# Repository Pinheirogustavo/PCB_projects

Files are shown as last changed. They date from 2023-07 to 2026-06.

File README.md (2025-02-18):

# PCB Projects

## Conexões presentes nas barras de pinos

### Barra de "tensoes"

- Earth: Terra virtual implementado com LM675
- VCC: +(MaxTensao da fonte utilizada / 2) Tensao NÃO regulada
- VEE:-(MaxTensao da fonte utilizada / 2)  Tensao NÃO regulada
- +9V: regulador 7809
- -9V: regulador 7909
- +5V: regulador 7805
- -5V: regulador 7905
- +3.3V: regulador 1117T-3.3

### Barra "Sinais analogicos"
- I1: corrente 1 dada pela fonte Howland
- I2: corrente 2 dada pela fonte Howland (caso bipolar)
- Ampl1: Tensão de saída condicionada do INA que monitora a corrente I1
- Ampl2: Tensão de saída condicionada do INA que monitora a corrente I2
- Sin1: Sinal alternado 1 gerado por AD9833/9850. Sem amplificação
- Sin2: Sinal alternado 2 gerado por AD9833/9850. Sem amplificação
- SinA: Sinal alternado 1 com controle de amplitude (talvez freq e fase)
- SinB: Sinal alternado 2 com controle de amplitude (talvez freq e fase)

### Barra "comunicacao"
- SINC: Sinal de sincronismo (ainda a definir)
- SDA(1-3)/SCL(1-3): Três pares de pinos reservados para comunicação - I2C
- SPI_COPI: comunicação SPI Controller Out Peripheral In
- SPI_CIPO: comunicação SPI Controller In, Peripheral Out
- SPI_clk: pino de clock que estabelece o sincronismo da comunicação SPI
- CS(x): pinos para selecionar o chip desejado (Chip Select)
> CS (AD9833): seleciona o gerador de sinais AD9833

> CS (X9c10x): seleciona o potenciometro digital do circuito de controle da corrente

###### comunicação I2C

SDA1/SCL1: implementado nos módulos "Gerador de sinais", com resistores pullup (Rp) para dispositivos de 3.3V;

SDA2/SCL2: implementado nos módulos "Fonte de corrente", com resistores pullup (Rp) para dispositivos de 5.0V. 

I2C arduino: https://docs.arduino.cc/learn/communication/wire

SPI arduino https://docs.arduino.cc/learn/communication/spi?_gl=1*1

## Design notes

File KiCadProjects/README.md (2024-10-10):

# Versao do CAD: KiCad 7.0    

Placa 900x100mm face dupla

## Dicas gerais de uso do KiCad

- Os projetos desenvolvidos na versão Kicad 7.0 não são compatíveis com versões mais recentes.

- Sempre que for alterar um projeto abra o "arquivo_pro" específico, não o arquivo geral "KiCadProjects.kicad_pro".

- Ao realizar alguma modificação de projeto elétrico (não somente design), Faça a alteração no arquivo esquemático "arquivo_sch" e depois altere o arquivo de design "arquivo_pcb" por meio da ferramenta de "atualize a PCI com as alterações feitas no esquema - F8" (símbolo no painel superior). Modificações realizadas no sentido contrário não são atualizadas no esquema e assim sua placa confeccionada não irá corresponder ao projeto elétrico criado.

- Um bom tutorial em vídeo pode ser encontrado na playlist: <https://youtube.com/playlist?list=PL3bNyZYHcRSUhUXUt51W6nKvxx2ORvUQB&si=-wXaexDJ6YDI0aJu>

- Ao criar os seus esquemas tente separar cada estágio ou módulo e evite realizar ligações diretas de "wire", pois isso irá deixar a leitura mais confusa. Ao invés disso, utilize "rótulos globais" (Ctrl L / etiqueta no painel direito), que funcionam como conectores e ainda indicam os nós dos circuitos.

## Criando simbolos, footprint e 3D  

- Editor de símbolos &rarr; Arquivo &rarr; Nova biblioteca &rarr; Global &rarr; acesse a pasta de bibliotecas do seu github &rarr; acesse a pasta dos simbolos criados por você &rarr; NOME_SIMBOLO.kicad_sym Salvar. 
 - clique em "Criar Novo Símbolo (N)" 
  
- Quando criar um novo simbolo procure seguir Reference designator: https://en.wikipedia.org/wiki/Reference_designator 
  
- Sempre utilize pinos passivos 
- Numere os pinos no desenho do símbolo, para que o footprint possa fazer a atribuição correta 
- Nome do simbolo: Duplo clique na area de trabalho &rarr; preencher o campo valor 

## Como adicionar bibliotecas  

- Bibliotecas prontas da internet (salvar em Projeto Global): https://forum.digikey.com/t/importing-the-digi-key-kicad-library-into-kicad-5-0-0/4075 
 caminho:/PCB_projects/KiCadProjects/libraries/ 
  
- Bibliotecas criadas pelo autor:  Usar o editor de simbolos e de footprint do kicad, salvar em Projeto Global.

    Caminho:/PCB_projects/KiCadProjects/libraries/MyCreates

    Já criados símbolos e footprints dos seguintes componentes:

        Módulo do gerador AD9833

        Módulo do gerador AD9850

        Módulo do Potenciômetro digital X9c10x

        Chave gangorra

- Sempre adicione as bibliotecas pelo github e não pela sua máquina local. Exemplo: 
    
 Errado: /home/name/PCB_projects/KiCadProjects/libraries/MyCreates/AD9833_module.pretty 
    
 Certo: /home/name/**github**/PCB_projects/KiCadProjects/libraries/MyCreates/AD9833_module.pretty 

 ###### Há nesse tutorial uma lista de footprints para os componentes mais comuns entre os circuitos. Utilize essa lista para garantir que haja espaço adequado a esses componentes em sua placa.

## Algumas das regras de layout PCB  - Fabricação JLCPCB

#### Todas as regras e restrições para a produção pela Jlcpcb devem ser conferidas em: <https://jlcpcb.com/capabilities/pcb-capabilities>

- largura dos segmentos de linha de corte ( Edge.cuts): 0.15 mm
  
- Tamanho de via: 0.30mm - 6.30mm diâmetro interno. Diâmetro externo deve ser no mínimo 0.20mm maior que o interno.

- Largura da trilha: mínimo de 0.16 mm (6.5 mils)

- Espaçamento entre trilhas: mínimo de 0.10 mm (4 mils)

- Espaçamento entre trilha e borda da via: mínimo de 0.10 mm (4 mils)

- Serigrafia: Largura mínima da linha de 0.16 mm (6 mils) e altura mínima do texto de 1.00 mm (40 mils).
    - Preferencialmente manter a proporção 1:6.

##### Todas essas restrições podem ser definidas por meio das "Regras de desenho" do Kicad.

 Símbolo de engrenagem (segundo no painel superior_ &rarr; Regras de desenho &rarr; tamanhos pré-definidos.
    - Permite estabelecer tamanhos de vias e trilhas que serão seguidas em todo o desenho.

 Símbolo de engrenagem (segundo no painel superior_ &rarr; Regras de desenho &rarr; restrições.
    - Permite estabalecer regras que se violadas serão indicadas pelo verificador de regras de desenho.

  Símbolo de engrenagem (segundo no painel superior_ &rarr; Texto & gráfico.
    - Permite estabelecer tamanho de Serigrafia que será seguido em todo o desenho.

##### Sempre execute o "Verificador de regras de desenho (símbolo de lista no painel superior) antes de gerar os arquivos para confecção.

- Extra: para produção na CNC - O grid deve ser maior que o diâmetro da fresa utilizada (>0,2mm).

## Orientações para layout PCB  

- Criar trilhas de alimentação, de terra e de clock. 
- Fazer as trilhas de alimentação com largura maior 
- Evitar trilhas muito longas 
- Preferir mudanças de direção de 45º nas trilhas 
- Evitar que trilhas de sinais críticos (clock e altas freqüências) fiquem paralelas por muito tempo 
- Evitar ligações diretas entre as entradas de alimentação de Cis 
- Colocar um LED indicando que a placa está energizada 
- Colocar pontos de acesso para medir com o osciloscópio 
- Usar soquetes para os CIs 
 
- Segundo ícone, ao lado do simbolo de disquete. Serve para editar as regras de furos, tamanhos de trilhas... sempre conferir. 
  
- Ícone de lista. Serve para verificar as regras RDC. 

## Alguns footprints de componentes comuns   

Resistor
    
    Resistor_THT:R_Axial_DIN0207_L6.3mm_D2.5mm_P7.62mm_Horizontal 

Capacitor eletrolítico
    
    Capacitor_THT:CP_Radial_D5.0mm_P2.50mm 

Capacitor cerâmico 
    
    Capacitor_THT:C_Disc_D3.0mm_W1.6mm_P2.50mm

Capacitor tântalo 
    
    Capacitor_THT:CP_Radial_Tantal_D4.5mm_P2.50mm 

Diodo
    
    Diode_THT:D_DO-41_SOD81_P10.16mm_Horizontal

LED 
    
    LED_THT:LED_D5.0mm 

conectores fêmea

    Connector_PinSocket_2.54mm:PinSocket_1xXX_P2.54mm_Vertical 

conectores macho 
   
    Connector_PinHeader_2.54mm:PinHeader_1xXX_P2.54mm_Vertical 

conector p4 de bateria 
    
    Connector_BarrelJack:BarrelJack_GCT_DCJ200-10-A_Horizontal 

chave gangorra
    
    Chave_Gangorra:chave gangorra 2 pinos
    
L7809
    
    Package_TO_SOT_THT:TO-220-3_Vertical
    
LM7909
    
    Package_TO_SOT_THT:TO-220-3_Vertical
    
LM675
    
    Package_TO_SOT_THT:TO-220-5_P3.4x3.7mm_StaggerOdd_Lead3.8mm_Vertical
    
L7805
    
    Package_TO_SOT_THT:TO-220-3_Vertical
    
L7905
    
    Package_TO_SOT_THT:TO-220-3_Vertical
    
LM1117T-3.3
    
    Package_TO_SOT_THT:TO-220-3_Vertical
    
AD9850
    
    Capacitor_THT:C_Disc_D3.0mm_W1.6mm_P2.50mm
    
STM32-bluepill
    
    BluePill_STM32:BluePill_STM32F103C
    
AD828
    
    AD828:AD828
    
Potenciômetro Digital X9c10x
    
    X9c10X_module:X9c10X_module
    
Arduino Nano
    
    Module:Arduino_Nano
    
AD9833
    
    AD9833_module:AD9833_module

## Tamanho de pad de componentes comuns   

###### Caso esteja usando a CNC, todos os furos podem ser configurados diretamente no FlatCAM, não sendo necessário defini-los no projeto do Kicad.

- Resistores 

>Forma da ilha: Oval
>
>Tamanho da ilha: 2,0x1,6mm
>
>Forma do furo: circular
>
>Diâmetro do furo: 0,8mm

- Capacitores eletrolíticos 

> Forma da ilha: oval(+)            retangular(-)
>
> Tamanho da ilha:2,0x1,6mm(+)      2,0x1,6mm(-)
>
> Forma do furo: circular(+)        circular(-)
>
> Diâmetro do furo: 0,8mm(+)        0,8mm(-)

- Diodos 

> Forma da ilha: oval(+)            retangular(-)
>
> Tamanho da ilha:2,0x1,6mm(+)      2,0x1,6mm(-)
>
> Forma do furo: circular(+)        circular(-)
>
> Diâmetro do furo: 0,8mm(+)        0,8mm(-) 

- LED 

> Forma da ilha: oval(+)            retangular(-)
>
> Tamanho da ilha:2,0x1,8mm(+)      1,8x1,8mm(-)
>
> Forma do furo: circular(+)        circular(-)
>
> Diâmetro do furo: 1,1mm(+)        1,1mm(-) 

- Barra de pinos 

> Forma da ilha: oval
>
> Tamanho da ilha: 2,5x1,8mm
>
> Forma do furo:circular
>
> Diâmetro do furo: 1,02
  
- Chave gangorra

> Forma da ilha: Retangular
>
> Tamanho da ilha: 2,5x7,0mm
>
> Forma do furo: oval
>
> Diâmetro do furo: 0,8x6,0mm

- Conector p4 de bateria 

    - pad1 (vin)
    
        > Forma da ilha: retangular
	
        > Tamanho da ilha: 4,6x2,0mm
	
        > Forma do furo: oval
	
        > Diâmetro do furo: 3,6x1,0mm_P2
        
    - pad2 (vee)
    
        > Forma da ilha: Oval
	
        > Tamanho da ilha: 4,2x2,0mm
	
        > Forma do furo: oval
	
        > Diâmetro do furo: 3,2x1,0mm
        
    - pad3
    
        > Forma da ilha: Oval
	
        > Tamanho da ilha: 2,0x4,2mm
	
        > Forma do furo: oval
	
        > Diâmetro do furo: 1,0x3,2mm

## Autoroteamento

-   Utilize o plugin Freerouting ou Grid Router
-   Antes de tudo sempre realize primeiramente a atualiação da PCB a partir do esquemático e a verifcação das regras de desenho
-   Caso deseje refazer o roteamento, exclua todas as trilhas e vias geradas anteriormente: Editar → Exclusões globais → Vias e trilhas/Todas as camadas.
-   Caso tenha criado uma “zona” (linha tracejada) para o plano terra, a remova antes de realizar novo Autoroteamento (Ver mais em:  [https://www.reddit.com/r/KiCad/comments/5eu7fo/freerouting_left_a_lot_of_grounds_unreachable/](https://www.reddit.com/r/KiCad/comments/5eu7fo/freerouting_left_a_lot_of_grounds_unreachable/))

## Envio para produção no JLCPCB

#### Todas as orientações para a produção pela Jlcpcb a partir do Kicad 7.0 devem ser conferidas em: <https://jlcpcb.com/help/article/how-to-generate-gerber-and-drill-files-in-kicad-7>

Em resumo, você deve gerar 3 tipos de arquivos: Gerber, de perfuração (drill) e o mapeamento do projeto.

- Gerar arquivos Gerber: Files &rarr; Fabrication outputs &rarr; Gerbers (.gbr)
    As seguintes camadas devem ser selecionadas:

        F.Cu

        F.Paste

        F.Silks

        F.Mask

        B.Cu

        B.Paste

        B.Silks

        B.Mask

        Edge.Cuts

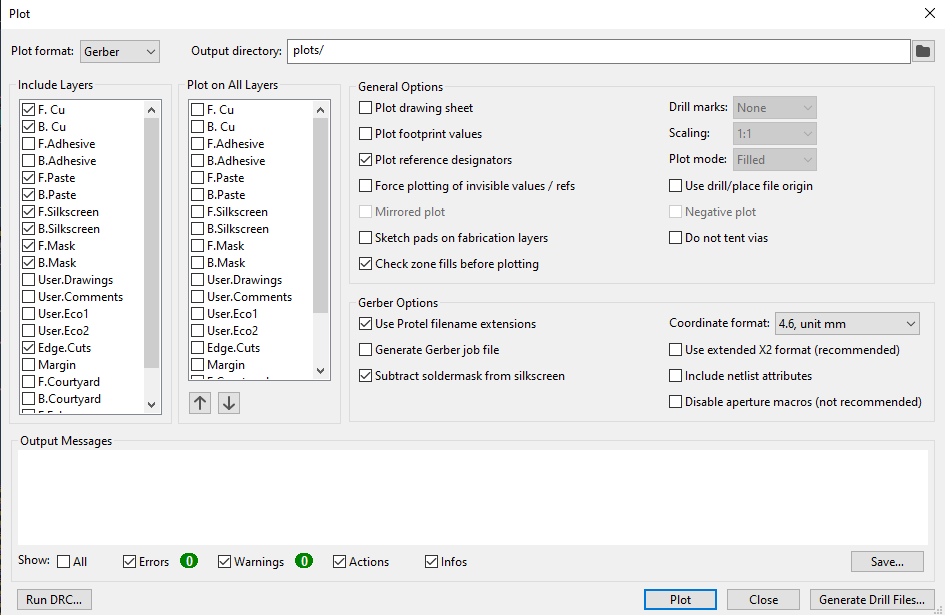
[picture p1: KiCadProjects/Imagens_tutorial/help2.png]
Camadas para gerber JLCPCB - Kicad

imagem retirada do site da JLCPCB

- Para gerar os arquivos de furo clique em "generate drill files" e siga as instruções:

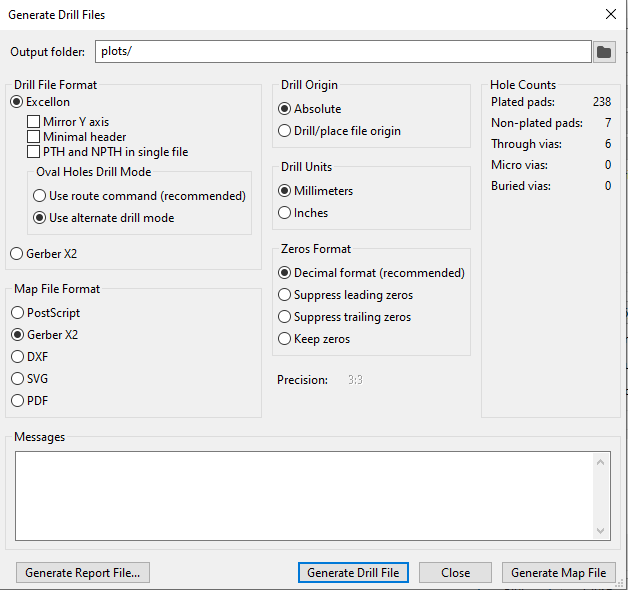
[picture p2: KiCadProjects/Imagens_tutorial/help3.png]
Furos para JLCPCB - Kicad

imagem retirada do site da JLCPCB

- Gere o arquivo de mapeamento clicando em "generate Map file".

- Todos os arquivos devem ser salvos em única pasta.

- Ao final a pasta deve conter 13 arquivos que são enviados para produção em .ZIP ou .RAR a partir da página inicial da fabricante.

#### Como produzir placas pequenas de modo repetido (Painel)

O tamanho mínimo das placas confeccionadas na JLCPCB é de 100x100mm. Caso a placa produzida seja menor, é possível copiar o design dentro de uma área definida. Há dois modos de realizar isso:

- Por meio do próprio site de encomenda do circuito. Em "PCB Specifications" selecione "Panel by JLCPCB". Ele irá captar as dimensões das linhas de "Edge.cuts" do projeto e assim você só precisa selecionar o número de linhas e colunas com repetição do projeto.

- Manualmente: Há um plugin, "Kikit", que auxilia esse trabalho. Uma vez instalado o circuito pode ser repetido por n linhas e m colunas com o uso da ferramenta "Kikit: Panelize PCB".

###### No momento de escrita desse tutorial não havia diferença de preço entre os modos de "panelização".

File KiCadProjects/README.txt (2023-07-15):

Versao do CAD: KiCad 7.0

------------------------------------------------------------------------------------------------------------------------------------------
Como adicionar bibliotecas

- Bibliotecas prontas da internet (salvar em Projeto Global): https://forum.digikey.com/t/importing-the-digi-key-kicad-library-into-kicad-5-0-0/4075
	caminho:/PCB_projects/KiCadProjects/libraries/

- Bibliotecas criadas pelo autor:  Usar o editor de simbolos e de footprint do kicad, salvar em Projeto Global
	caminho:/PCB_projects/KiCadProjects/libraries/MyCreates
------------------------------------------------------------------------------------------------------------------------------------------

Placa 90x100mm face simples

Trilhas azuis: trilhas dispostas na face de cobre inferior

Trilhas vermelhas: Representam jumpers, estao dispostas na face de cobre superior

------------------------------------------------------------------------------------------------------------------------------------------

Regras de layout PCB

- largura da trilha = 50 mils (1,27 mm)
 	O valor mínimo é de 8 mils, mas isso gera uma trilha extremamente fina
- Espaçamento entre trilhas = 50 mils (1,27 mm)
	O grid deve ser maior que o diâmetro da fresa utilizada (>0,2mm)
- Definir o algoritmo de auto-roteamento no CAD como “Grid Router” (precisa adicionar plugin)
- Definir o diâmetro do contorno em 0,5mm

------------------------------------------------------------------------------------------------------------------------------------------

Orientações para layout PCB

- Criar trilhas de alimentação, de terra e de clock.
- Fazer as trilhas de alimentação com largura maior
- Evitar trilhas muito longas
- Preferir mudanças de direção de 45º nas trilhas
- Evitar que trilhas de sinais críticos (clock e altas freqüências) fiquem paralelas por muito tempo
- Evitar ligações diretas entre as entradas de alimentação de Cis
- Colocar um LED indicando que a placa está energizada
-Colocar pontos de acesso para medir com o osciloscópio
- Usar soquetes para os CIs

------------------------------------------------------------------------------------------------------------------------------------------
Alguns footprints de componentes comuns e suas melhores  escolhas (ou até achar algo melhor)

Resistores -  11779 Resistor_THT:R_Axial_DIN0207_L6.3mm_D2.5mm_P7.62mm_Horizontal
Capacitores eletrolíticos - 525 Capacitor_THT:CP_Radial_D5.0mm_P2.50mm
Diodos -  7485 Diode_THT:D_DO-41_SOD81_P10.16mm_Horizontal
LED - 8642 LED_THT:LED_D5.0mm
conectores fêmea -  5813/6090 Connector_PinSocket_2.54mm:PinSocket_1xXX_P2.54mm_Vertical
conectores macho -  4855/5132 Connector_PinHeader_2.54mm:PinHeader_1xXX_P2.54mm_Vertical 
conector p4 de bateria - 1150 Connector_BarrelJack:BarrelJack_GCT_DCJ200-10-A_Horizontal

------------------------------------------------------------------------------------------------------------------------------------------
Tamanho de pad de componentes comuns e suas melhores  escolhas (ou até achar algo melhor). O tamanho do furo (0,8mm) não precisa ser configurado agora pois pode ser modificado na hora da produção (FlatCAM).

Resistores -  circular 2,5mm 
Capacitores eletrolíticos -  	+ circular 2mm	-retangular2x2,5mm
Diodos -   circular 2,5mm 
LED - 	+ circular 2mm	-retangular2x2,5mm
Barra de pinos - circular 2mm
conector p4 de bateria - oval3x4,2mm retangular4,6x3mm

------------------------------------------------------------------------------------------------------------------------------------------
FONTE DE TENSAO

v01;v02 SW1: Botão DPDT com trava para ligar e desligar a fonte. https://www.multcomercial.com.br/chave-push-button-7x7-com-trava.html
v03;v04 Chave gangorra kcd1 para ligar e desligar a fonte.

Os reguladores estao localizados na borda da placa, alinhados e igualmente espaçados, sendo possivel utilizar único dissipador

Segundo icone, ao lado do simbolo de disquete. Para editar as regras de furos, tamanhos de trilhas... sempre conferir. 

Icone de lista. Verifica as regras.

------------------------------------------------------------------------------------------------------------------------------------------

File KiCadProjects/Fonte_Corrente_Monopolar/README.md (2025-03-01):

# Fonte de corrente monopolar

## Versão atualmente implementada no tomógrafo: V02

## Descrição Geral do projeto

Fonte de corrente controlada por tensão monopolar do tipo Howoland aperfeiçoada. O Sistema é excitado por um sinal senoidal e fornece uma corrente alternada de amplitude constante frente uma banda de resistências. Há um sistema de monitoramento da amplitude da corrente (Ampl1) que é implementado com um circuito de condicionamento dedicado.

Estágios Fonte de Corrente: Sinal de entrada(Sin1 ou SinA) &rarr; buffer &rarr; arquitetura fonte Howland &rarr; Resistor Sentinela//Amplificador de Instrumentação &rarr;  corrente I1.

Estágios monitoramento: Amplificador de Instrumentação &rarr; AmpOp &rarr; circuito de condicionamento &rarr; amplitude da corrente Ampl1.

## Componentes do circuito:

- Amplificador Operacional Dual AD826/828: Amplificador operacional duplo implementado como buffer na entrada do sistema e de acordo com a arquitetura da fonte Howland aperfeiçoada.
	>Amplificador 1: buffer.
	
	>Amplificador 2: arquitetura da fonte Howland aperfeiçoada.
- Resistor sentinela: Resistor de baixa resistência em série com a saída da fonte Howland. Implementado para monitorar a corrente gerada.
- Amplificador de Instrumentação INA: Amplificador de Instrumentação verifica a tensão sobre o resistor sentinela e aplica alto ganho fixo. A tensão de saída é condicionada e indica a amplitude da corrente (Ampl1).  Implementado para monitorar a corrente gerada. 
- Circuito de condicionamento: Condiciona o sinal para os limites do ADC do controlador (Selecionado com jumpers nos pinos "Vref" 3.3/5V). 

## Cuidados a serem tomados

## Estágios do circuito

#### Entrada do sinal de controle de corrente:

O sinal de entrada (Vin) determina a amplitude e frequência da corrente gerada. O sistema permite dois sinais de entrada, Sin1 e SinA, que são selecionados por uma chave gangorra kcd1.

A frequência da corrente é a mesma do sinal de entrada Vin. A amplitude da corrente é dada por:

$$ I = \frac{V_{in}}{R_6} $$

#### Buffer:

Buffer implementado na entrada do sistema com o amplificador operacional dual uma vez que o circuito do gerador de sinais foi projetado sem buffer em sua saída.

#### Arquitetura fonte Howland:

Fonte monopolar do tipo Howland aperfeiçoada.

#### Resistor sentinela e amplificador de instrumentação

#### Circuito de condicionamento

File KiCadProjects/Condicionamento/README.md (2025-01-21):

# Placa de condicionamento de sinal

## Versões em produção (jlcpcb):condicionamento_compacto_V01a; condicionamento_compacto_V01b; condicionamento_Aquisicao_BIA_v03

## Descrição Geral do projeto

Circuito de condicionamento de sinal para aquisição por microcontrolador.

# Versões do projeto:

## condicionamento_compacto_V01

Circuito projetado para apenas condicionar o sinal de interesse para correta aquisição do microcontrolador utilizado, buscando não alterar nenhuma característica do sinal.

Estágios: Sinais a serem condicionados &rarr; buffer &rarr; offset (valor médio do limite de entrada do ADC) &rarr; diodos de proteção ( limites de entrada do ADC) &rarr; Filtro anti-aliasing &rarr; sinal condicionado &rarr; ADC@uC

O circuito de condicionamento permite a adequada aquisição de sinal por meio de microcontrolador, garantindo que os sinais aplicados nas entradas do dispositivo não ultrapassem os limites de tensão e corrente suportados, além da adequada amostragem do sinal, por meio de filtro anti-aliasing. Esse circuito emprega o amplificador operacional dual, o que permite o condicionamento de dois canais. Os estágios do circuito são:

- buffer: amplificador operacional no modo seguidor, configuração de alta impedância de entrada que permite o adequado acoplamento entre os estágios do sistema, minimizando a interação entre eles.

- Offset: estágio que realiza um deslocamento (offset) do sinal de entrada, adequando os sinais alternados de correntes do circuito aos ADCs do microcontrolador, adicionando um sinal DC equivalente ao valor médio do limite de entrada dos ADCS. O valor de Vref pode ser escolhido por um pino de entrada do circuito.

- Diodos de proteção: não permitem que o sinal de entrada ultrapasse  os limites de entrada do conversor ADC.

- filtro anti-alising: Frequência de corte $F_c$:

$$F_c = \frac{1}{2\cdot\pi\cdot R\cdot C} = \frac{1}{2\cdot\pi\cdot220\cdot470\cdot10 ^{-12}} = 1,5 MHz$$
**ALTERAR LEVANDO EM CONTA OS OUTROS COMPONENTES**

## condicionamento_compacto_V02

Circuito projeto para, além de condicionar o sinal de interesse para os limites de operação do microcontrolador, aplicar um ganho ao sinal de interesse em busca de melhorar a relação sinal-ruído obtida.

Estágios: Sinais a serem condicionados &rarr; buffer &rarr; amplificador não inversor com variação da resistência de entrada por controle eletrônico  &rarr; offset (valor médio do limite de entrada do ADC) &rarr; diodos de proteção ( limites de entrada do ADC) &rarr; Filtro anti-aliasing &rarr; sinal condicionado &rarr; ADC@uC

## condicionamento_Aquisicao_BIA_v01

Circuito projetado para condicionamento e aquisição de apenas 4 canais para um Analisador de Bioimpedância.

## condicionamento_Aquisicao_BIA_v02

Circuito projetado para condicionamento e aquisição de apenas 4 canais para um Analisador de Bioimpedância.

## condicionamento_Aquisicao_BIA_v03

Circuito projetado para condicionamento e aquisição de apenas 4 canais para um Analisador de Bioimpedância.

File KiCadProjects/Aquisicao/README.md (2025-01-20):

# Placa de Aquisição 

## Versão atual em produção (jlcpcb:): 01

## Descrição Geral do projeto
 As placas de aquisição tem a função de suportar os módulos de microcontroladores stm32 modelo bluepill, empregados na demodulação de sinais.

### Versão 01

Esta versão suporta até 4 módulos stm32 bluepill. Onde é possível demodular 4 ou 8 canais externos em cada módulo.

A versão de barramento suportada é:

A alimentação de cada módulo é "dedicada". Isto é, há um regulador de tensão StepDown implementado na placa que fornece a tensão de 5V (5V_stepdown), que é regulada a 3.3V (3,3V_step) que é empregada na alimentação dos módulos. Em resumo os estágios são:

VCC (barramento) &rarr; 5V (StepDown) &rarr; 3V (regulador) &rarr; entrada 3.3V bluepill

As entradas analógicas fixas de cada módulo são:

> PA1 - Amplitude da corrente I1 (Ampl1)

> PA4 - Amplitude da corrente I2 (Ampl2)

As entradas analógicas de cada módulo referentos aos canais externos são:

> PA0 - Canal X (sign_Cx)

> PB0 - Canal X+4 (sign_Cx+4)

>Estes canais externos não estão implementados no barramento, mas sim por conectores de pinos horizontais laterais identificados por "sign_C" (elementos J4 e J5).

As conexões de comunicação de cada módulo são (I2C):

> PB6 - SCL1 (3.3V)

> PB7 - SDA1 (3.3V)

As entradas digitais reservadas para sinais de sincronismo são:

> PA5 - SINC_A

> PA6 - SINC_B

> PA7 - SINC_C

> PB1 - SINCD

Assim, a ideia é que a placa opere em dois modos:

- Modo 1: leitura da amplitude de corrente individualmente em cada microcontrolador.
    Dado que o microcontrolador opera com dois ADCs, um estaria dedicado a ler algum sinal de corrente (I1 ou I2) e o segundo dedicado a ler um dos sinais vindos dos canais externos), possibilitando a leitura de 4 canais por placa de aquisição.

- Modo 2: leitura apenas dos canais externos por cada microcontrolador, sem leitura da corrente.
    Nesse modo os dois ADCs de cada microcontrolador realizam a leitura dos dois canais externos (X) e (X+4), possibilitando a leitura de 8 canais por placa de aquisição.

### Versao 02

### Versão 03

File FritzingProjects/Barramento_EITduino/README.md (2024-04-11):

# AVISO IMPORTANTE: Este Barramento está desatualizado em relação ao barramento mais recente e implementado nas novas placas do projeto. Para o barramento atualizado, ver Kicad-BarramentoV04 

O barramento para o Fritzing será atualizado o mais breve possível.

#### Esquemático

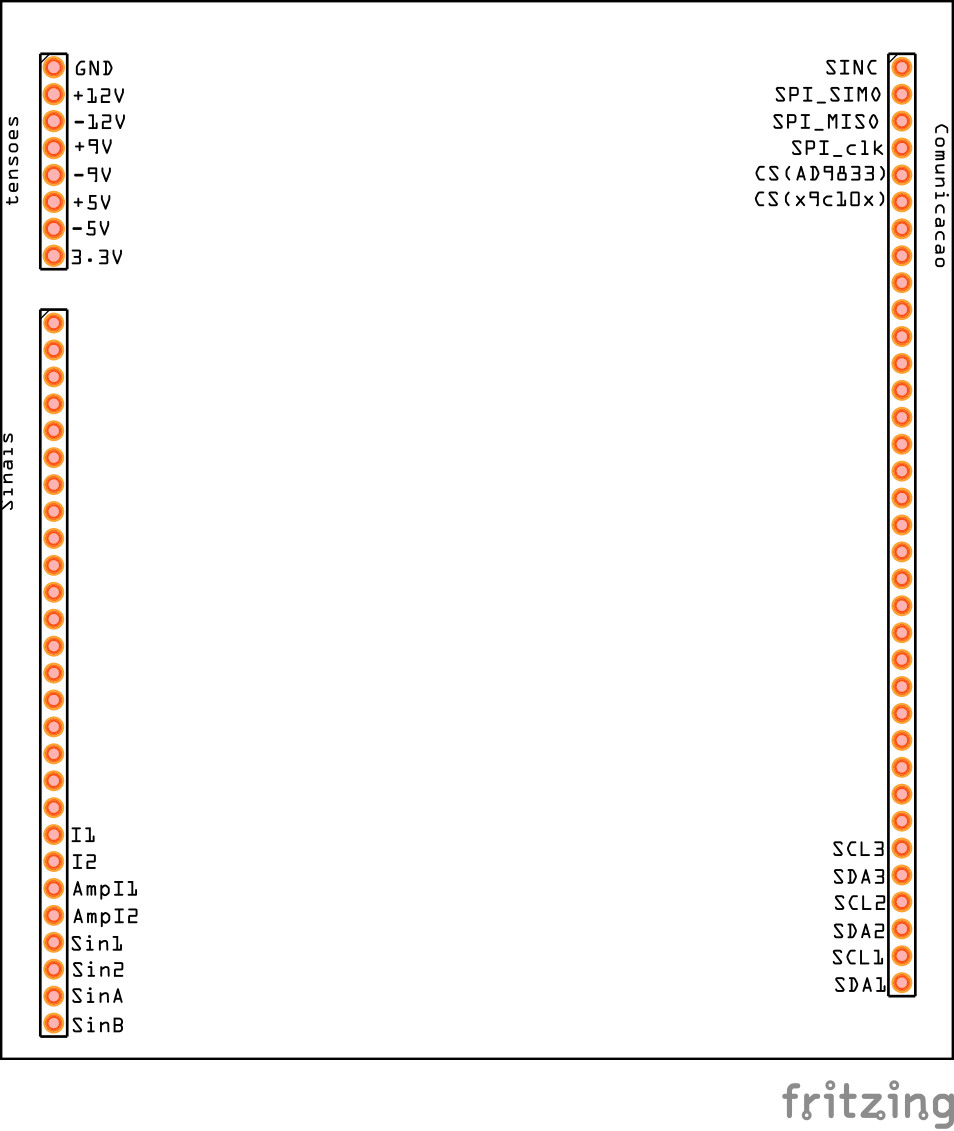
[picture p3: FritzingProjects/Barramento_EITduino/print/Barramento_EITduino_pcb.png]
Barramento EITduino - Fritzing


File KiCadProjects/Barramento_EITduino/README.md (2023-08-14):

# PCB Projects

## V01

Apresenta um único pino de terra

## V02 

- Apresenta diversos pontos de terras, separados em terras dos sinais analógicos (AGND) e terras dos sinais digitais (DGND).
- As alimentações dos circuitos analógicos foram separadas das alimentações dos circuitos digitais.

## Conexões presentes nas barras de pinos

### "tensoes"

- AGND: Terra virtual implementado com LM675 - circuitos analógicos
- DGND: Terra virtual implementado com LM675 - circuitos digitais
- VCC: +(MaxTensao da fonte utilizada / 2) Tensao NÃO regulada
- VEE:-(MaxTensao da fonte utilizada / 2)  Tensao NÃO regulada
- +9V: regulador 7809
- -9V: regulador 7909
- +5V: regulador 7805
- -5V: regulador 7905
- +3.3V: regulador 1117T-3.3

### "Sinais analogicos"
- I1: corrente 1 dada pela fonte Howland
- I2: corrente 2 dada pela fonte Howland (caso bipolar)
- Ampl1: Tensão de saída condicionada do INA que monitora a corrente I1
- Ampl2: Tensão de saída condicionada do INA que monitora a corrente I2
- Sin1: Sinal alternado 1 gerado por AD9833/9850. Sem amplificação
- Sin2: Sinal alternado 2 gerado por AD9833/9850. Sem amplificação
- SinA: Sinal alternado 1 com controle de amplitude (talvez freq e fase)
- SinB: Sinal alternado 2 com controle de amplitude (talvez freq e fase)

### "comunicacao"
- SINC: Sinal de sincronismo (ainda a definir)
- SDA(1-3)/SCL(1-3): Três pares de pinos reservados para comunicação - I2C
- SPI_COPI: comunicação SPI Controller Out Peripheral In
- SPI_CIPO: comunicação SPI Controller In, Peripheral Out
- SPI_clk: pino de clock que estabelece o sincronismo da comunicação SPI
- CS(x): pinos para selecionar o chip desejado (Chip Select)
> CS (AD9833): seleciona o gerador de sinais AD9833

> CS (X9c10x): seleciona o potenciometro digital do circuito de controle da corrente

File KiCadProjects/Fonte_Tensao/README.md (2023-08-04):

# Fonte de tensão

## Versão atual em protótipo: 03

## Descrição Geral do projeto

Sistema que a partir de uma fonte de tensão comum gera uma fonte de tensão simétrica com diferentes saídas de tensões reguladas para alimentação de todo o EITduino.

Estágios: Fonte de tensão comum ($\geqslant$ 24V) &rarr; Terra virtual &rarr; saída simétrica não regulada VCC VEE &rarr;
	> Saídas reguladas simétricas para alimentação analógica: +9V/-9V 
	> Saídas reguladas; +5V/-5V
	> Saída regulada:+3.3V

## Componentes do circuito:

- LM675
- LM78XX
- LM79XX
- LM117T-3.3

## Cuidados a serem tomados

Os reguladores da série 78XX podem ser agrupados em um único dissipador, o mesmo vale para os reguladores da série 79XX. Todos os outros dissipadores devem ser mantidos afastados pois suas carcaças não se encontram no mesmo potencial do sistema. 

O AmpOp LM675 apresenta elevada dissipação de energia, sempre utilize um dissipador de calor. 

## Estágios do circuito

#### Terra virtual

O terra virtual é feito com o amplificador operacional LM675, que fornece uma corrente máxima de 1,5A. Sua saída é simétrica em VCC +(MaxTensao da fonte utilizada / 2) e em VEE -(MaxTensao da fonte utilizada / 2).

Essas tensões não são reguladas, sofrendo oscilações e não devem ser utilizadas para alimentação de outros subsistemas do EITduino.

#### Reguladores 78XX

Reguladores de tensão positivos que também fornecem corrente máxima de 1,5A. São utilizados CIs que fornecem +9V e +5V.

#### Reguladores 79XX

Reguladores de tensão negativos que também fornecem corrente máxima de 1,5A. São utilizados CIs que fornecem -9V e -5V.

#### Regulador LM117T-3.3

Regulador de tensão positivo que  fornece corrente máxima de 800mA. Fornece +3.3V.

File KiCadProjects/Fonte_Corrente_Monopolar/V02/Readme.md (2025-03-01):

### Os esquemático e visão-3D podem ser conferidos em alta resolução na pasta [print](https://github.com/Pinheirogustavo/PCB_projects/tree/main/KiCadProjects/Fonte_Corrente_Monopolar/V02/print)

## Esquemático

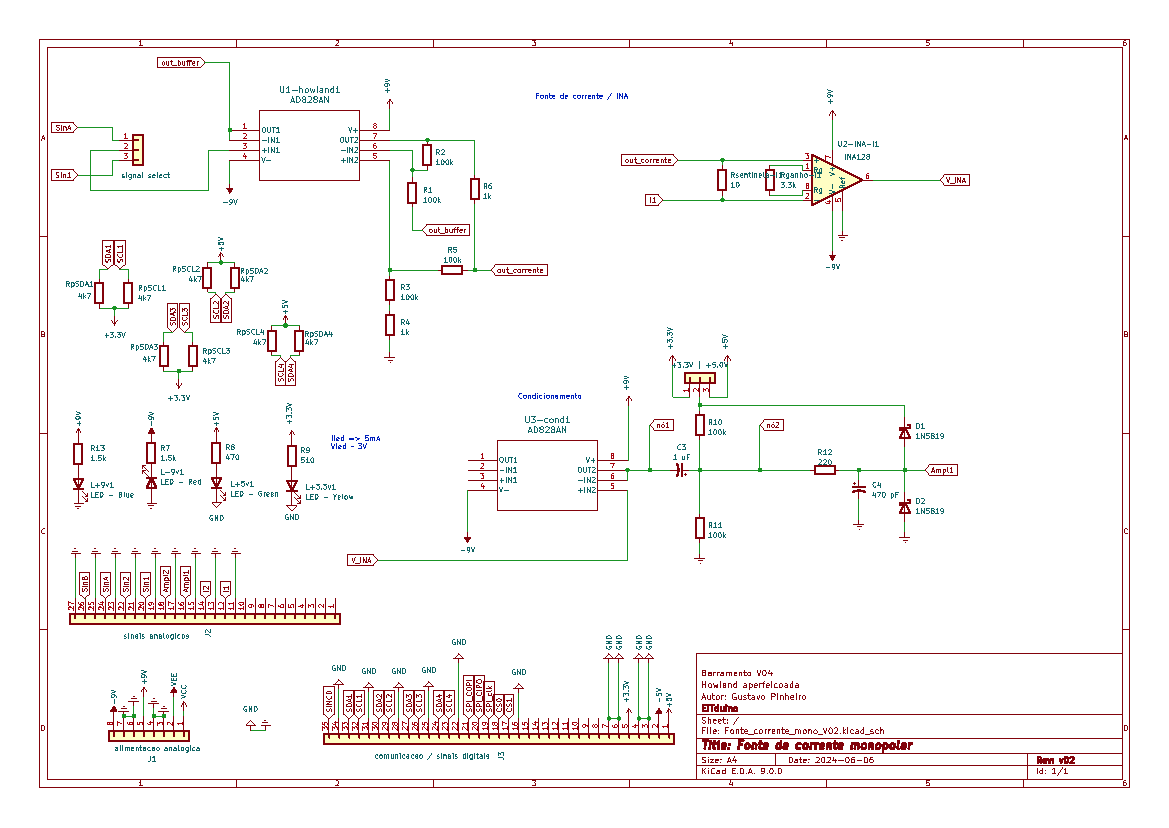
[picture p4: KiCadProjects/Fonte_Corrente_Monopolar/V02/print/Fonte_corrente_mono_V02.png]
Fonte de corrente howland aperfeiçoada monopolar - Kicad


## PCB-3D

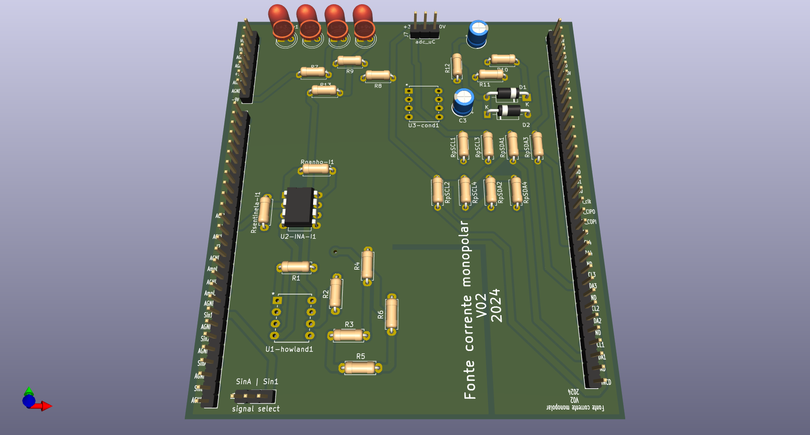
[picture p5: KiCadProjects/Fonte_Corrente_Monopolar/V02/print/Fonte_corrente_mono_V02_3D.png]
Fonte de corrente howland aperfeiçoada monopolar - PCB 3D Kicad


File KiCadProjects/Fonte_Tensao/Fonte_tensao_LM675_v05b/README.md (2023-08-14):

# V02

- Diversos pontos de terras, separados em terras dos sinais analógicos (AGND) e terras dos sinais digitais (DGND).
- As alimentações dos circuitos analógicos foram separadas das alimentações dos circuitos digitais.

# Esquemático

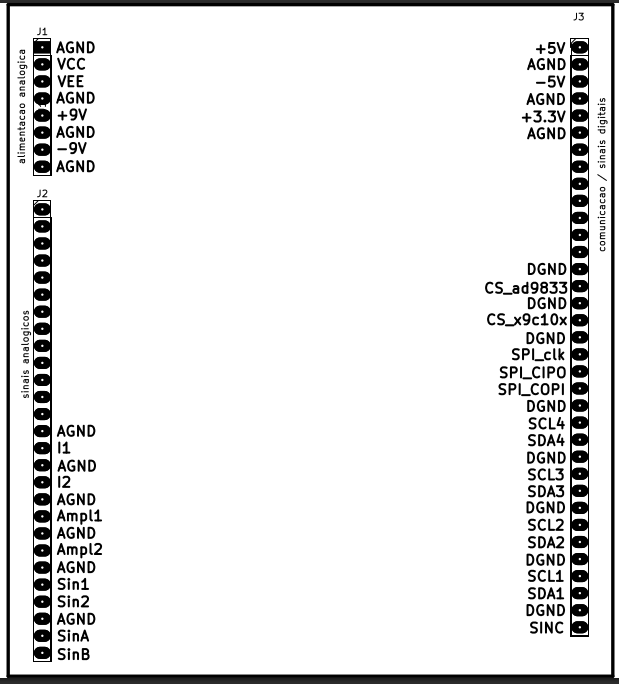
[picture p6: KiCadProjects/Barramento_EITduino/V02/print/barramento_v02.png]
Barramento EITduino V02 preto e branco - Kicad


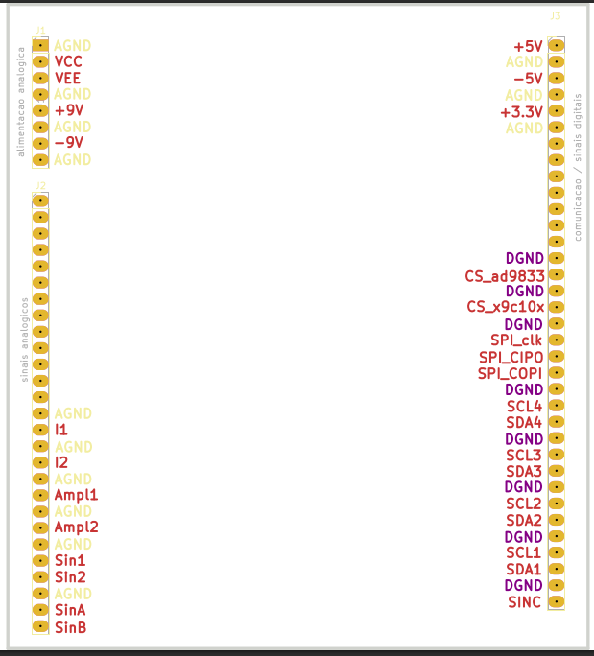
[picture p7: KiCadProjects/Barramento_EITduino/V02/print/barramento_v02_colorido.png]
Barramento EITduino V02 colorido - Kicad


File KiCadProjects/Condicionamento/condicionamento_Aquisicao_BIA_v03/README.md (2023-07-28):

# Circuito de condicionamento e aquisição de sinal

## Descrição Geral do projeto

Sistema projetado para permitir a aquisição de sinais por meio dos dois ADCs presentes em cada microcontrolador STM32.

Estágios: Sinais a serem condicionados &rarr; buffer &rarr; offset (valor médio do limite de entrada do ADC) &rarr; diodos de proteção ( limites de entrada do ADC) &rarr; Filtro anti-aliasing &rarr; sinal condicionado &rarr; ADC@STM32

## Sinais do circuito:

- AmplI1: Tensão de saída **já condicionada** do INA que monitora a corrente I1
- Amp_E1: Tensão medida pelo eletrodo proximal do pé/mão
- Amp_E2: Tensão medida pelo eletrodo proximal do pé/mão

##Cuidados a serem tomados

O conjunto de pinos **Vref** permite selecionar sinais e 3.3V e 5.0V. A escolha do sinal deve ser adequada ao limite de entrada dos pinos ADCs do microcontrolador utilizado. Para o STM32 esse limite é de 3.3V.

Todos os sinais que são enviados aos pinos de ADCs dos microcontroladores devem estar devidamente condicionados.

Sobre a alimentação dos microcontroladores: O par de pinos "alimentacao_Master" fornece uma alimentação de +5V  ao Master quando é fechado. Esse  par de pinos deve permanecer aberto quando o microcontrolador Master estiver conectado ao computador por meio de cabo USB, pois o pino de 5V do STM32 é diretamente conectada à alimentação fornecida por USB, sem qualquer circuito de proteção. O microcontrolador Slave está sempre conectado à alimentação de 5V do sistema. Somente conecte esse dispositivo ao computador se o sistema estiver desligado. 

## Estágios do circuito

#### Circuito de condicionamento

O circuito de condicionamento permite a adequada aquisição de sinal por meio de microcontrolador, garantindo que os sinais aplicados nas entradas do dispositivo não ultrapassem os limites de tensão e corrente suportados, além da adequada amostragem do sinal, por meio de filtro anti-aliasing. Esse circuito emprega o amplificador operacional dual AD826/828, o que permite o condicionamento de dois canais. Os estágios do circuito são: 

- buffer: amplificador operacional no modo seguidor, configuração de alta impedância de entrada que permite o adequado acoplamento entre os estágios do sistema, minimizando a interação entre eles.

- Offset: estágio que realiza um deslocamento (offset) do sinal de entrada, adequando os sinais alternados de correntes do circuito aos ADCs do microcontrolador, adicionando um sinal DC equivalente ao valor médio do limite de entrada dos ADCS. O valor de Vref deve ser definido pelo operador de acordo com esse limite.

- Diodos de proteção: não permitem que o sinal de entrada ultrapasse  os limites de entrada do conversor ADC. O valor de Vref deve ser definido pelo operador de acordo com esse limite.

- filtro anti-alising: Frequência de corte $F_c$:

$$F_c = \frac{1}{2\cdot\pi\cdot R\cdot C} = \frac{1}{2\cdot\pi\cdot220\cdot470\cdot10 ^{-12}} = 1,5 MHz$$

#### Microcontroladores

Dois microcontroladores são empregados nesse sistema de BIA, permitindo a leitura de 4 canais de medição. A comunicação entre eles é feita por meio do protocolo I2C. Ambos leem o sinal de amplitude da corrente medida pelo INA (AmpI1) em seus ADCs.

- STM32 Master

O par de pinos "alimentacao_Master" fornece uma alimentação de +5V quando é fechado. Esse  par de pinos deve permanecer aberto quando o microcontrolador estiver conectado ao computador por meio de cabo USB, pois o pino de 5V do STM32 é diretamente conectada à alimentação fornecida por USB, sem qualquer circuito de proteção.

> ADC1: Pino B0 recebe o sinal de amplitude de corrente AmpI1

> ADC2: Pino B1 recebe o sinal de amplitude de tensão do eletrodo de medição E1.

- STM32 Slave

O microcontrolador está sempre conectado à alimentação de 5V do sistema. Somente conecte esse dispositivo ao computador se o sistema estiver desligado. 

> ADC1: Pino B0 recebe o sinal de amplitude de corrente AmpI1

> ADC2: Pino B1 recebe o sinal de amplitude de tensão do eletrodo de medição E2.

## Esquemático

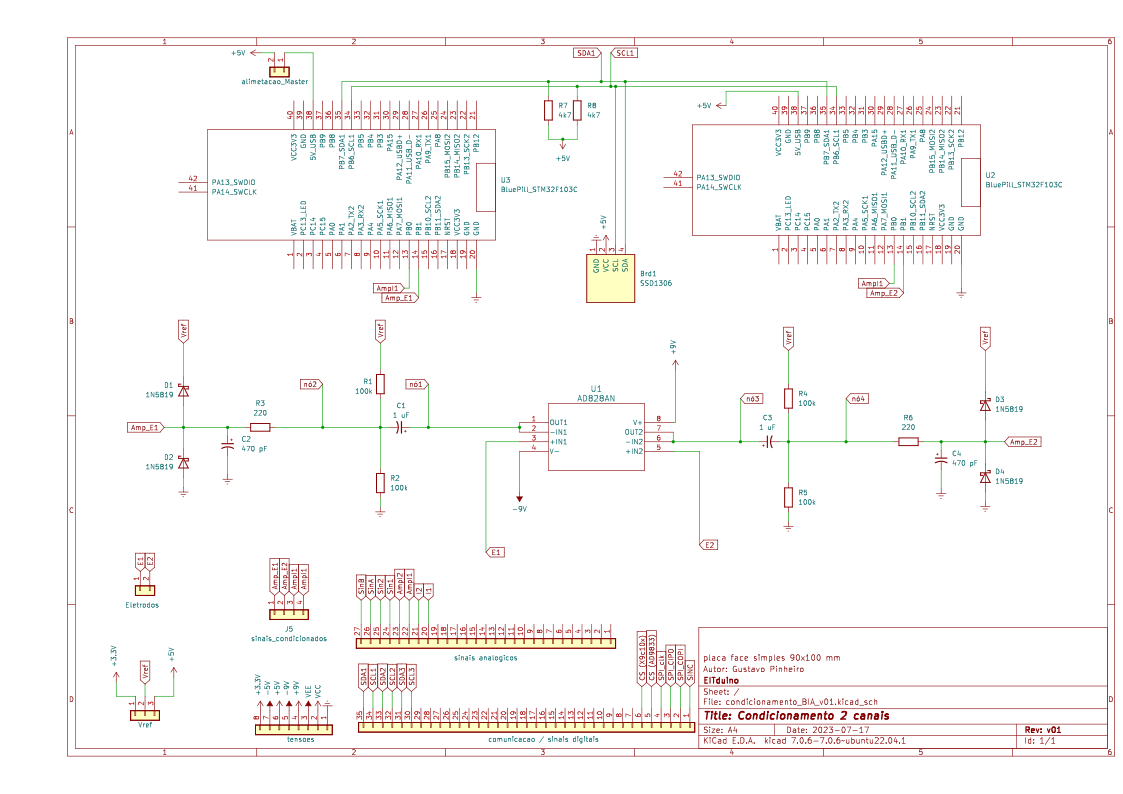
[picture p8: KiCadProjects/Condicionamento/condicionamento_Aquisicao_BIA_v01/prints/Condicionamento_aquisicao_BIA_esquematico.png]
Legenda Esquematico- Kicad


## PCB

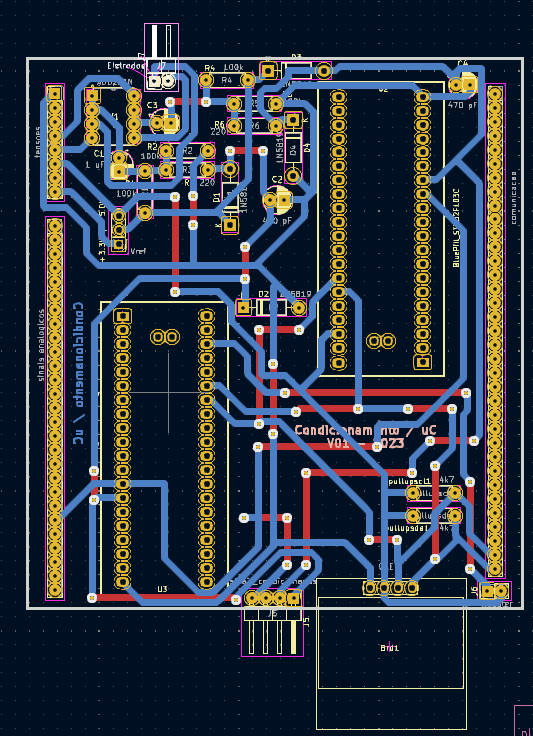
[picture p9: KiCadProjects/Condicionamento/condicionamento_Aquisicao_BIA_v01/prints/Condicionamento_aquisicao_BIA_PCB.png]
Legenda PCB- Kicad


## PCB-3D

legenda PCB 3D - Kicad

## PCB Máscara

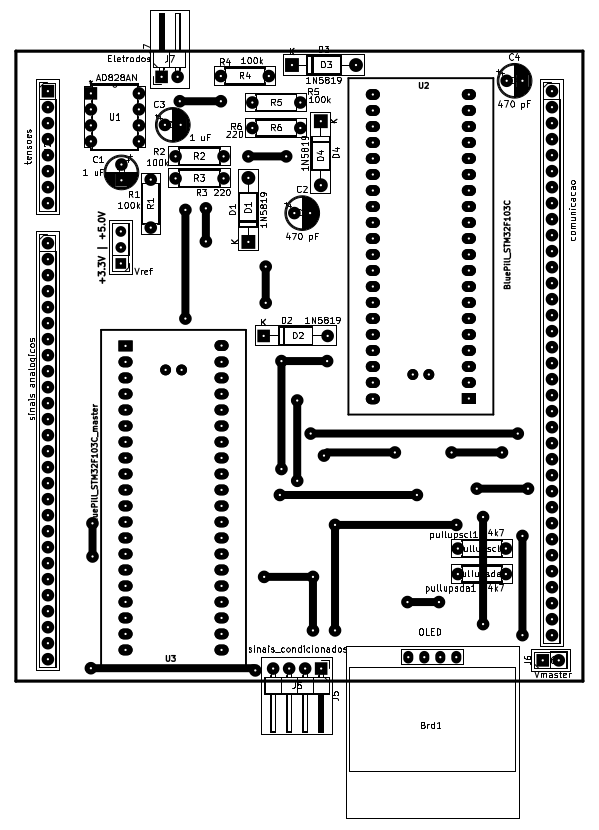
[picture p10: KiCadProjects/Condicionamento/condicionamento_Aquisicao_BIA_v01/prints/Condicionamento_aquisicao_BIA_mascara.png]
legenda PCB Máscara - Kicad


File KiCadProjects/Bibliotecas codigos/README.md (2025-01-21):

# Bibliotecas para uso de microcontroladores (.h)

Aqui estão reunidas todas as bibliotecas empregadas nos microcontroladores presentes no projeto de tomógrafo por impedância elétrica desse repositório. A intenção é permitir que se rastreie quais versões das bibliotecas estão implementadas nesse projeto, visto que elas são utilizadas e modificadas por outros pesquisadores do grupo.

A seguir a descrição dessas bibliotecas:

## AD9833.h

> Autoria: Bill Williams

> Modificado por: não modificado

Biblioteca para controle do módulo gerador de onda AD9833 por meio de comunicação SPI. Funciona apenas com o microcontrolador Arduino Nano. **É necessário, como próximo passo, adaptá-la para o microcontrolador stm32**.

## ad9850.h

> Autoria:  Erick León

> Modificado por: Gustavo Pinheiro

Biblioteca para controle do módulo gerador de onda AD9850 por meio de saídas digitais de um microcontrolador qualquer. As únicas alterações foram justamente nos pinos digitais utilizados em cada projeto de placa.

**Para futuras aplicações** deve-se apenas alterar os pinos digitais utilizados para o controle (linhas 8 a 11).

## demux.h

> Autoria: Gustavo Pinheiro

> Modificado por:

Biblioteca para o uso da placa demux "Demux.V01". Permitindo selecionar os canais de injeção e drenagem de corrente num universo de 128 eletrodos.

A seleção do canal é feita a partir de um byte, dividido da seguinte forma:

> In (injeção): 0000 0000 to 0111 1111 or 00 to 7F or 0 to 127

> Out (drenagem): 1000 0000 to 1111 1111 or 80 to FF or 128 to 255

Uma  pode ser encontrada em:
Você pode consultar uma [tabela ASCII](https://web.cecs.pdx.edu/~harry/compilers/ASCIIChart.pdf) para verificar o valor hexadecimal de um eletrodo específico, uma vez que os bytes enviados pela comunicação I2C estão nesse formato.

**Atualmente os projetos de placas se limitam a 32 canais, 5 mux's em cascata. A integração de mais placas ou aumento de canais em cada uma delas necessita de alteração da Biblioteca para expansão na manipulação dos bits**

## dft.h

> Autoria:  Erick León

> Modificado por:

A Biblioteca permite o cálculo de uma componente da DFT de um sinal qualquer, se amostrado um sinal com ciclos completos (ou seja, em uma frequência que seja múltipla inteira da frequência de amostragem).

Retorna:

> Valor medio do sinal

> A amplitude do sinal

> A fase do sinal

## gerador.h

> Autoria: Gustavo Pinheiro

> Modificado por:

A Biblioteca permite controlar a placa de gerador de sinais "AD9850.V01", alterando a frequência do sinal emitido pelo módulo ad9850 e controle do ganho de sinal, por meio de alteração do potenciômetro implementado no amplificador inversor.

As funções presentes são:

> incrementa_frequencia(): Aumenta a frequência do sinal emitido, percorrendo um array de valores.

> decrementa_frequencia(): Diminui a frequência do sinal emitido, percorrendo um array de valores.

> aumenta_ganho(): Aumenta o ganho do sinal emitido, percorrendo para baixo os valores do potenciômetro digital (wiper_down).

> diminui_ganho(): Diminui o ganho do sinal emitido, percorrendo para cima os valores do potenciômetro digital (wiper_up).

> ganho_minimo(): Configura o circuito para o ganho mínimo possível.

> ganho_maximo(): Configura o circuito para o ganho máximo possível.

> printa_dados(): Exibe no monitor serial os valores de resitência do potenciômetro digital e a frequência do sinal atuais.

## serial_debug.h

> Autoria: Erick León

> Modificado por:

## stm32_adc_dual_mode.h

> Autoria: Erick León

> Modificado por:

Biblioteca para uso do ADC do STM32F103.

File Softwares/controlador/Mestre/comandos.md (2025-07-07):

Lista de comandos para o programa de controle mestre EIT "Mestre.ino"
# Comandos de seleção de frequências

- **1**: altera a frequência do sinal para **200 kHz**; n_pontos_base = 3; n_pontos_mult = 2 (= 2 ciclos); tempo de demodulacao = 2.

- **2**: altera a frequência do sinal para **125 kHz**; n_pontos_base = 24; n_pontos_mult = 1 (= 5 ciclos); tempo de demodulacao = 10.

- **3**: altera a frequência do sinal para **100 kHz**; n_pontos_base = 6; n_pontos_mult = 2 (= 2 ciclos); tempo de demodulacao = 5.

- **4**: altera a frequência do sinal para **50 kHz**; n_pontos_base = 12; n_pontos_mult = 2 (= 2 ciclos); tempo de demodulacao = 10.

- **5**: altera a frequência do sinal para **5 kHz**; n_pontos_base = 120; n_pontos_mult = 2 (= 2 ciclos); tempo de demodulacao = 10.

# Parâmetros de demodulação

- **-**: Diminui o tempo de demodulação.

- **+**: Aumenta o tempo de demodulação.

- **t**: Diminui número de pontos da demodulação.

- **u**: Aumenta número de pontos da demodulação.

# Controle de eletrodos

- **a**: Injeta nos eletrodos 0 e 1.

- **b**: Injeta nos eletrodos 1 e 2.

- **c**: Injeta nos eletrodos 2 e 3.

- **w**: Diminui padrão de injeção.

- **z**: Aumenta padrão de injeção.

# Modos de leitura

- **i**: Inicia as medidas dos eletrodos.

- **v**: Pega os valores lidos pelos eletrodos.

- **f**: Pega um frame da leitura.

- **m**: Pega um frame da leitura e exibe a matriz.

- **j**:

- **k**:

- **l**:

- **s**:

# Controle de amplitude do sinal

- **L**: Diminui a amplitude do sinal.

- **U**: Aumenta a amplitude do sinal.

- **S**: Salva o ganho do sinal.

- **x**: Reduz o sinal ao ganho mínimo.

- **y**: Aumenta o sinal ao ganho máximo.

- **p**: Imprime os dados do sinal: Valor do resistor de ganho (Rs); frequência atual; ganho atual; tensão de saida ideal.

# xxxxx

- **adicionar enderecos dos dispositivos**:

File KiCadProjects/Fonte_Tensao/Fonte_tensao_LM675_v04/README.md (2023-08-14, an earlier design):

# Fonte de tensão

## Especificidades da versão

A base do barramento é a  [versão 2 do barramento EITduino](https://github.com/Pinheirogustavo/PCB_projects/tree/main/KiCadProjects/Barramento_EITduino/V02)

LED vermelho: indica que uma fonte externa está conectada e acionada.

LED verde: indica o funcionamento do circuito de terra virtual.

Foram adicionados diversos pinos de terra AGND e DGND em relação às versões anteriores.

## Cuidados a serem tomados

## Esquemático

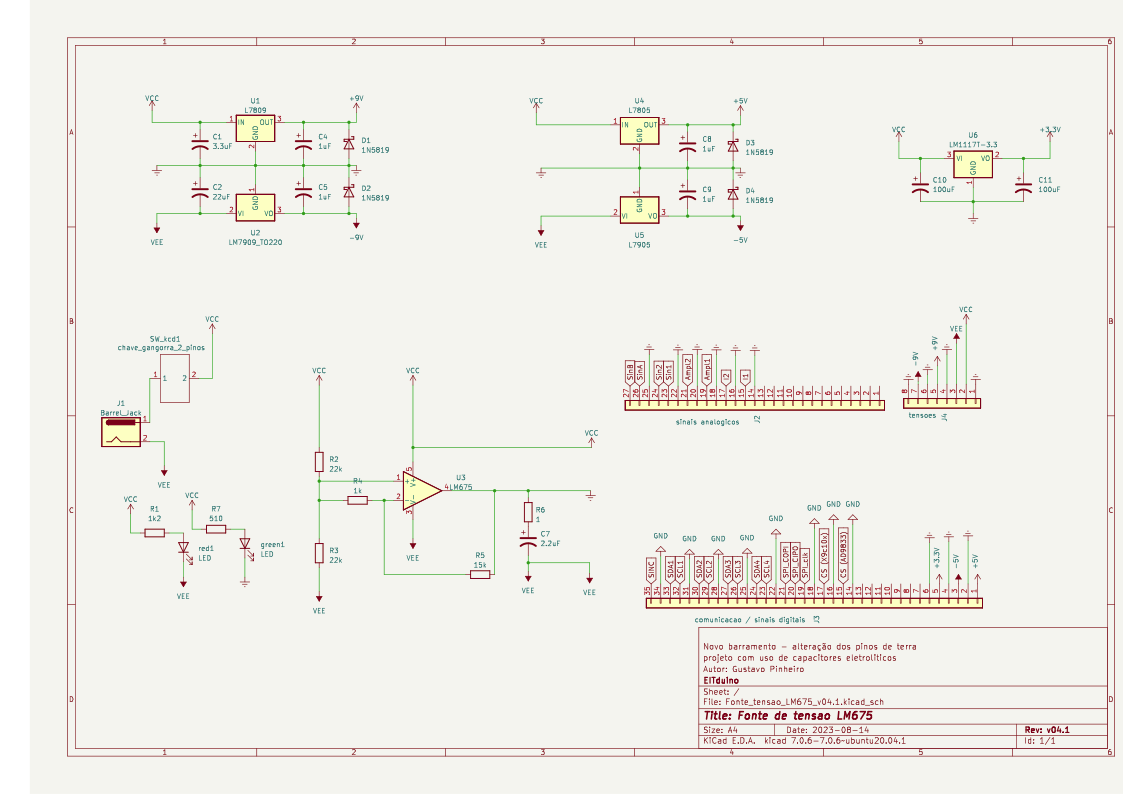
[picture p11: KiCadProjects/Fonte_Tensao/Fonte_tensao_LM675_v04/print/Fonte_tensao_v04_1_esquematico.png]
Legenda Esquematico- Kicad


## PCB

Legenda PCB- Kicad

## PCB-3D

legenda PCB 3D - Kicad

## PCB Máscara

legenda PCB Máscara - Kicad

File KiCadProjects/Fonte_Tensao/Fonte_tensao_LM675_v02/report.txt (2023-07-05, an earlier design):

Traçado para '/home/gustavo/Dropbox/KiCadProjects/Fonte_Tensao/Fonte_tensao_LM675_v02/gerbers/Fonte_tensao_LM675-F_Cu.gbr'.
Traçado para '/home/gustavo/Dropbox/KiCadProjects/Fonte_Tensao/Fonte_tensao_LM675_v02/gerbers/Fonte_tensao_LM675-B_Cu.gbr'.
Traçado para '/home/gustavo/Dropbox/KiCadProjects/Fonte_Tensao/Fonte_tensao_LM675_v02/gerbers/Fonte_tensao_LM675-F_Paste.gbr'.
Traçado para '/home/gustavo/Dropbox/KiCadProjects/Fonte_Tensao/Fonte_tensao_LM675_v02/gerbers/Fonte_tensao_LM675-B_Paste.gbr'.
Traçado para '/home/gustavo/Dropbox/KiCadProjects/Fonte_Tensao/Fonte_tensao_LM675_v02/gerbers/Fonte_tensao_LM675-F_Silkscreen.gbr'.
Traçado para '/home/gustavo/Dropbox/KiCadProjects/Fonte_Tensao/Fonte_tensao_LM675_v02/gerbers/Fonte_tensao_LM675-B_Silkscreen.gbr'.
Traçado para '/home/gustavo/Dropbox/KiCadProjects/Fonte_Tensao/Fonte_tensao_LM675_v02/gerbers/Fonte_tensao_LM675-F_Mask.gbr'.
Traçado para '/home/gustavo/Dropbox/KiCadProjects/Fonte_Tensao/Fonte_tensao_LM675_v02/gerbers/Fonte_tensao_LM675-B_Mask.gbr'.
Traçado para '/home/gustavo/Dropbox/KiCadProjects/Fonte_Tensao/Fonte_tensao_LM675_v02/gerbers/Fonte_tensao_LM675-Edge_Cuts.gbr'.
Arquivo de trabalho do Gerber '/home/gustavo/Dropbox/KiCadProjects/Fonte_Tensao/Fonte_tensao_LM675_v02/gerbers/Fonte_tensao_LM675-job.gbrjob' foi criado.
Informação: Feito.

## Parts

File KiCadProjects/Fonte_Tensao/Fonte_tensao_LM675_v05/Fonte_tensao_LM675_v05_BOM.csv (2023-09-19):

Id | Designador | Footprint | Quantidade | Designação | Fornecedor e referência | itens para 5 placas?
1 | D1,D4,D3,D2 | D_DO-41_SOD81_P10.16mm_Horizontal | 4 | 1N5819 |  | ok
2 | C5 | C_Disc_D3.0mm_W1.6mm_P2.50mm | 1 | 220nF |  | n
3 | R7 | R_Axial_DIN0207_L6.3mm_D2.5mm_P7.62mm_Horizontal | 1 | 1 |  | Somente 10 ohms
4 | U2 | TO-220-3_Vertical | 1 | LM7909_TO220 |  | n
5 | R5 | R_Axial_DIN0207_L6.3mm_D2.5mm_P7.62mm_Horizontal | 1 | 1k |  | n
6 | C4,C1,C10,C7 | CP_Radial_Tantal_D4.5mm_P2.50mm | 4 | 1uF
7 | C8 | CP_Radial_Tantal_D4.5mm_P2.50mm | 1 | 10uF
8 | R3,R4 | R_Axial_DIN0207_L6.3mm_D2.5mm_P7.62mm_Horizontal | 2 | 22k |  | n
9 | U3 | TO-220-5_P3.4x3.7mm_StaggerOdd_Lead3.8mm_Vertical | 1 | LM675
10 | I/0 | chave gangorra 2 pinos | 1 | Vin
11 | green1,red1 | LED_D5.0mm | 2 | LED
12 | J3 | PinHeader_1x35_P2.54mm_Vertical | 1 | comunicacao / sinais digitais
13 | C9 | CP_Radial_Tantal_D4.5mm_P2.50mm | 1 | 33uF
14 | C11,C2 | CP_Radial_Tantal_D4.5mm_P2.50mm | 2 | 2.2uF
15 | U5 | TO-220-3_Vertical | 1 | L7905
16 | J1 | PinHeader_1x08_P2.54mm_Vertical | 1 | alimentacao analogica
17 | J2 | PinHeader_1x27_P2.54mm_Vertical | 1 | sinais analogicos
18 | U6 | TO-220-3_Vertical | 1 | LM1117T-3.3
19 | C3,C12 | C_Disc_D3.0mm_W1.6mm_P2.50mm | 2 | 100 nF
20 | R2 | R_Axial_DIN0207_L6.3mm_D2.5mm_P7.62mm_Horizontal | 1 | 510 |  | n
21 | R6 | R_Axial_DIN0207_L6.3mm_D2.5mm_P7.62mm_Horizontal | 1 | 15k |  | n
22 | U1 | TO-220-3_Vertical | 1 | L7809
23 | U4 | TO-220-3_Vertical | 1 | L7805
24 | Vin | BarrelJack_GCT_DCJ200-10-A_Horizontal | 1 | Vin
25 | R1 | R_Axial_DIN0207_L6.3mm_D2.5mm_P7.62mm_Horizontal | 1 | 1k2 |  | n

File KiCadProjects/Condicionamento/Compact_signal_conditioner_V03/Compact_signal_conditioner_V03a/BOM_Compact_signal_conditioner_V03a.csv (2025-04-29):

Reference | Qty | Value | DNP | Exclude from BOM | Exclude from Board | Footprint | Datasheet
C1,C4 | 2 | 470 pF |  |  |  | Capacitor_THT:CP_Radial_D5.0mm_P2.50mm | ~
C2,C3 | 2 | 1 uF |  |  |  | Capacitor_THT:CP_Radial_D5.0mm_P2.50mm | ~
D1,D2,D3,D4 | 4 | 1N5819 |  |  |  | Diode_THT:D_DO-41_SOD81_P10.16mm_Horizontal | http://www.vishay.com/docs/88525/1n5817.pdf
J1 | 1 | Conn_02x09_Top_Bottom |  |  |  | Connector_PinSocket_2.54mm:PinSocket_2x09_P2.54mm_Horizontal | ~
J2 | 1 | Canais-eletrodos |  |  |  | Connector_PinHeader_2.54mm:PinHeader_1x02_P2.54mm_Vertical | ~
J5 | 1 | in |  |  |  | Connector_PinSocket_2.54mm:PinSocket_1x06_P2.54mm_Horizontal | ~
J6 | 1 | In_1 select |  |  |  | Connector_PinHeader_2.54mm:PinHeader_1x03_P2.54mm_Vertical | ~
J7 | 1 | In_2 select |  |  |  | Connector_PinHeader_2.54mm:PinHeader_1x03_P2.54mm_Vertical | ~
J8 | 1 | out |  |  |  | Connector_PinHeader_2.54mm:PinHeader_1x06_P2.54mm_Horizontal | ~
R1,R8 | 2 | 220 |  |  |  | Resistor_THT:R_Axial_DIN0207_L6.3mm_D2.5mm_P7.62mm_Horizontal | ~
R2,R3,R4,R5 | 4 | 100k |  |  |  | Resistor_THT:R_Axial_DIN0207_L6.3mm_D2.5mm_P7.62mm_Horizontal | ~
RC1,RC2,RC3,RC4,RC5,RC6,RC7,RC8,RC9,RC10 | 10 | R |  |  |  | Resistor_THT:R_Axial_DIN0207_L6.3mm_D2.5mm_P7.62mm_Horizontal | ~
Rfg_1,Rfg_2 | 2 | 51k |  |  |  | Resistor_THT:R_Axial_DIN0207_L6.3mm_D2.5mm_P7.62mm_Horizontal | ~
U1,U2 | 2 | CD4066BE |  |  |  | Package_DIP:DIP-14_W7.62mm | https://www.ti.com/lit/ds/symlink/cd4066b.pdf
U1-buffer1,U2-gain1,U3-Cond-DIP1 | 3 | AD828AN |  |  |  | AD828:N_8_ADI | AD828AN
U4-Cond-SMD1,U5-buffer1,U6-gain1 | 3 | AD8056ARZ |  |  |  | AD8056:R_8_ADI | AD8056ARZ

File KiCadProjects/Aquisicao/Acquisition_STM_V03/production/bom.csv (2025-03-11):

Designator | Footprint | Quantity | Value | LCSC Part #
C1 | CP_Radial_D5.0mm_P2.50mm | 1 | 680u
C2 | CP_Radial_D5.0mm_P2.50mm | 1 | 220u
C3 | CP_Radial_Tantal_D4.5mm_P2.50mm | 1 | 10uF
C4 | CP_Radial_Tantal_D4.5mm_P2.50mm | 1 | 33uF
D1 | D_DO-41_SOD81_P10.16mm_Horizontal | 1 | 1N5819
J1 | PinHeader_1x08_P2.54mm_Vertical | 1 | alimentacao analogica
J10 | PinHeader_2x08_P2.54mm_Vertical | 1 | gpio-U1
J11 | PinHeader_2x08_P2.54mm_Vertical | 1 | gpio-U2
J12 | PinHeader_2x08_P2.54mm_Vertical | 1 | gpio-U3
J13 | PinHeader_2x08_P2.54mm_Vertical | 1 | gpio-U4
J14, J15, J16, J17, J18, J19, J8, J9 | PinHeader_2x05_P2.54mm_Horizontal | 8 | Conn_02x05_Top_Bottom
J2 | PinHeader_1x27_P2.54mm_Vertical | 1 | sinais analogicos
J3 | PinHeader_1x35_P2.54mm_Vertical | 1 | comunicacao / sinais digitais
L+3.3V1 | LED_D5.0mm | 1 | LED Yelow
L1 | L_7.3x7.3_H4.5 | 1 | 33u
R1 | R_Axial_DIN0207_L6.3mm_D2.5mm_P7.62mm_Horizontal | 1 | 510
U1, U2, U3, U4 | BluePill_STM32F103C | 4 | BluePill_STM32F103C
U5 | TO-220-5_P3.4x3.7mm_StaggerOdd_Lead3.8mm_Vertical | 1 | LM2596S-5
U6 | TO-220-3_Vertical | 1 | LM1117T-3.3

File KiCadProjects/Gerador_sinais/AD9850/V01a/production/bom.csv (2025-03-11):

Designator | Footprint | Quantity | Value | LCSC Part #
C3, C4 | C_Disc_D3.0mm_W1.6mm_P2.50mm | 2 | 100nF
J1 | PinHeader_1x08_P2.54mm_Vertical | 1 | alimentacao analogica
J2 | PinHeader_1x27_P2.54mm_Vertical | 1 | sinais analogicos
J3 | PinHeader_1x35_P2.54mm_Vertical | 1 | comunicacao / sinais digitais
J4 | PinHeader_1x02_P2.54mm_Vertical | 1 | 3.3V STM32
R11, R12 | R_Axial_DIN0207_L6.3mm_D2.5mm_P7.62mm_Horizontal | 2 | 2.2k
U1-AD9850 | AD9850_module | 1 | AD9850_module
U2 | BluePill_STM32F103C | 1 | BluePill_STM32F103C

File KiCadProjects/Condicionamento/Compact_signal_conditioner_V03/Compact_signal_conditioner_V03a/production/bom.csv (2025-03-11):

Designator | Footprint | Quantity | Value | LCSC Part #
C1, C4 | CP_Radial_D5.0mm_P2.50mm | 2 | 470 pF
C2, C3 | CP_Radial_D5.0mm_P2.50mm | 2 | 1 uF
D1, D2, D3, D4 | D_DO-41_SOD81_P10.16mm_Horizontal | 4 | 1N5819
J1 | PinSocket_2x09_P2.54mm_Horizontal | 1 | Conn_02x09_Top_Bottom
J2 | PinHeader_1x02_P2.54mm_Vertical | 1 | Canais-eletrodos
J5 | PinSocket_1x06_P2.54mm_Horizontal | 1 | in
J6 | PinHeader_1x03_P2.54mm_Vertical | 1 | In_1 select
J7 | PinHeader_1x03_P2.54mm_Vertical | 1 | In_2 select
J8 | PinHeader_1x06_P2.54mm_Horizontal | 1 | out
R1, R8 | R_Axial_DIN0207_L6.3mm_D2.5mm_P7.62mm_Horizontal | 2 | 220
R2, R3, R4, R5 | R_Axial_DIN0207_L6.3mm_D2.5mm_P7.62mm_Horizontal | 4 | 100k
RC1, RC10, RC2, RC3, RC4, RC5, RC6, RC7, RC8, RC9 | R_Axial_DIN0207_L6.3mm_D2.5mm_P7.62mm_Horizontal | 10 | R
RFG_1, RFG_2 | R_Axial_DIN0207_L6.3mm_D2.5mm_P7.62mm_Horizontal | 2 | 51k
U1, U2 | DIP-14_W7.62mm | 2 | CD4066BE
U1-BUFFER1, U2-GAIN1, U3-COND-DIP1 | N_8_ADI | 3 | AD828AN
U4-COND-SMD1, U5-BUFFER1, U6-GAIN1 | R_8_ADI | 3 | AD8056ARZ

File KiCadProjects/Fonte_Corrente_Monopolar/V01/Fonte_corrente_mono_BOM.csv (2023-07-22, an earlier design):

Id | Designador | Footprint | Quantidade | Designação | Fornecedor e referência
1 | J1 | PinHeader_1x03_P2.54mm_Vertical | 1 | Vref
2 | R12 | R_Axial_DIN0207_L6.3mm_D2.5mm_P7.62mm_Horizontal | 1 | 220
3 | Rsentinela1 | R_Axial_DIN0207_L6.3mm_D2.5mm_P7.62mm_Horizontal | 1 | 10
4 | C4 | CP_Radial_D5.0mm_P2.50mm | 1 | 470 pF
5 | U2 | DIP-8_W7.62mm | 1 | INA128
6 | J4 | PinSocket_1x35_P2.54mm_Vertical | 1 | comunicacao / sinais digitais
7 | U3-cond1,U1-howland1 | N_8_ADI | 2 | AD828AN
8 | R10,R1,R2,R11,R3,R5 | R_Axial_DIN0207_L6.3mm_D2.5mm_P7.62mm_Horizontal | 6 | 100k
9 | J2 | PinSocket_1x08_P2.54mm_Vertical | 1 | tensoes
10 | J3 | PinSocket_1x27_P2.54mm_Vertical | 1 | sinais analogicos
11 | RganhoINA1 | R_Axial_DIN0207_L6.3mm_D2.5mm_P7.62mm_Horizontal | 1 | 3,3k
12 | C3 | CP_Radial_D5.0mm_P2.50mm | 1 | 1 uF
13 | D2,D1 | D_DO-41_SOD81_P10.16mm_Horizontal | 2 | 1N5819
14 | SW_kcd1 | chave gangorra 3 pinos | 1 | sw
15 | R4,R6 | R_Axial_DIN0207_L6.3mm_D2.5mm_P7.62mm_Horizontal | 2 | 1k

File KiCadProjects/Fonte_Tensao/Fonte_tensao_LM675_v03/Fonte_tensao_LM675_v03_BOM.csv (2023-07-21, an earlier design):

Id | Designador | Footprint | Quantidade | Designação | Fornecedor e referência
1 | J1 | BarrelJack_GCT_DCJ200-10-A_Horizontal | 1 | P4 alimentação
2 | U3 | TO-220-5_P3.4x3.7mm_StaggerOdd_Lead3.8mm_Vertical | 1 | LM675
3 | C2 | CP_Radial_D5.0mm_P2.50mm | 1 | 22uF
4 | R1,R4 | R_Axial_DIN0617_L17.0mm_D6.0mm_P20.32mm_Horizontal | 2 | 1kΩ
5 | D2,D4,D3,D1 | D_DO-41_SOD81_P10.16mm_Horizontal | 4 | 1N5819
6 | U1 | TO-220-3_Vertical | 1 | L7809
7 | C10,C11 | CP_Radial_D5.0mm_P2.50mm | 2 | 10uF
8 | J3 | PinHeader_1x35_P2.54mm_Vertical | 1 | comunicacao / sinais digitais
9 | SW_kcd1 | chave gangorra 2 pinos | 1 | chave_gangorra_2_pinos
10 | U6 | TO-220-3_Vertical | 1 | LM1117T-3.3
11 | C9,C8,C5,C4 | CP_Radial_D5.0mm_P2.50mm | 4 | 1uF
12 | R5 | R_Axial_DIN0617_L17.0mm_D6.0mm_P20.32mm_Horizontal | 1 | 15kΩ
13 | U2 | TO-220-3_Vertical | 1 | LM7909_TO220
14 | J4 | PinHeader_1x08_P2.54mm_Vertical | 1 | tensoes
15 | J2 | PinHeader_1x27_P2.54mm_Vertical | 1 | sinais analogicos
16 | R2,R3 | R_Axial_DIN0617_L17.0mm_D6.0mm_P20.32mm_Horizontal | 2 | 22kΩ
17 | U4 | TO-220-3_Vertical | 1 | L7805
18 | U5 | TO-220-3_Vertical | 1 | L7905
19 | C7 | CP_Radial_D5.0mm_P2.50mm | 1 | 2.2uF
20 | C1 | CP_Radial_D5.0mm_P2.50mm | 1 | 3.3uF
21 | R6 | R_Axial_DIN0617_L17.0mm_D6.0mm_P20.32mm_Horizontal | 1 | 1Ω
22 | D5 | LED_D5.0mm | 1 | LED

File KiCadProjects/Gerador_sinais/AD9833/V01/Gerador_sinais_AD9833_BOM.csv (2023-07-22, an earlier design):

Id | Designador | Footprint | Quantidade | Designação | Fornecedor e referência
1 | U2 | X9c10X_module | 1 | X9c10x
2 | SW3 | SW_BUTT-2 | 1 | botao_decremento_freq
3 | C1 | CP_Radial_D5.0mm_P2.50mm | 1 | 100 nF
4 | A1 | Arduino_Nano | 1 | Arduino_Nano_v3.x
5 | U1 | N_8_ADI | 1 | AD828AN
6 | SW4 | SW_BUTT-2 | 1 | botao_save_Rgain
7 | J4 | PinHeader_1x35_P2.54mm_Vertical | 1 | comunicacao / sinais digitais
8 | SW6 | SW_BUTT-2 | 1 | botao_diminui_Rgain
9 | R2 | R_Axial_DIN0204_L3.6mm_D1.6mm_P5.08mm_Horizontal | 1 | 2,7k
10 | J1 | PinHeader_1x08_P2.54mm_Vertical | 1 | tensoes
11 | J3 | PinHeader_1x27_P2.54mm_Vertical | 1 | sinais analogicos
12 | U3 | AD9833_module | 1 | AD9833_module
13 | SW2 | SW_BUTT-2 | 1 | botao_incremento_freq
14 | SW1 | SW_BUTT-2 | 1 | botao_forma_onda
15 | R1 | R_Axial_DIN0204_L3.6mm_D1.6mm_P5.08mm_Horizontal | 1 | 10k
16 | SW5 | SW_BUTT-2 | 1 | botao_aumenta_Rgain

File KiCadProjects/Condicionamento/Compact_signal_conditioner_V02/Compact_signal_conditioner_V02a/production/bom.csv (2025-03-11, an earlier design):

Designator | Footprint | Quantity | Value | LCSC Part #
C1, C4 | CP_Radial_D5.0mm_P2.50mm | 2 | 470 pF
C2, C3 | CP_Radial_D5.0mm_P2.50mm | 2 | 1 uF
CF1-SELECT1 | PinHeader_1x02_P2.54mm_Vertical | 1 | jumper cf1
CF1A1, CF1B1, CF2A1, CF2B1 | CP_Radial_D5.0mm_P2.50mm | 4 | C
CF2-SELECT2 | PinHeader_1x02_P2.54mm_Vertical | 1 | jumper cf2
D1, D2, D3, D4 | D_DO-41_SOD81_P10.16mm_Horizontal | 4 | 1N5819
J3 | PinHeader_2x08_P2.54mm_Horizontal | 1 | Entrada
J4 | PinSocket_1x06_P2.54mm_Horizontal | 1 | in
J5 | PinHeader_1x06_P2.54mm_Horizontal | 1 | out
J6 | PinHeader_1x02_P2.54mm_Vertical | 1 | Canais
J7 | PinHeader_1x03_P2.54mm_Vertical | 1 | In_1 select
J8 | PinHeader_1x03_P2.54mm_Vertical | 1 | In_2 select
R1, R8 | R_Axial_DIN0207_L6.3mm_D2.5mm_P7.62mm_Horizontal | 2 | 220
R10, R11 | R_Axial_DIN0207_L6.3mm_D2.5mm_P7.62mm_Horizontal | 2 | 51k
R2, R3, R4, R5 | R_Axial_DIN0207_L6.3mm_D2.5mm_P7.62mm_Horizontal | 4 | 100k
U1-BUFFER1, U2-GAIN1, U3-COND-DIP1 | N_8_ADI | 3 | AD828AN
U4-COND-SMD1, U5-BUFFER1, U6-GAIN1 | R_8_ADI | 3 | AD8056ARZ
U4-DIGPOT2, U5-DIGPOT1 | X9c10X_module | 2 | X9c10x

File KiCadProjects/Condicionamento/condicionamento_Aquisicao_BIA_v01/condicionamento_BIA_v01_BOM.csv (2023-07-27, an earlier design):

Id | Designador | Footprint | Quantidade | Designação | Fornecedor e referência
1 | R5,R2,R1,R4 | R_Axial_DIN0207_L6.3mm_D2.5mm_P7.62mm_Horizontal | 4 | 100k
2 | Brd1 | 128x64OLED | 1 | OLED
3 | R3,R6 | R_Axial_DIN0207_L6.3mm_D2.5mm_P7.62mm_Horizontal | 2 | 220
4 | D3,D4,D1,D2 | D_DO-41_SOD81_P10.16mm_Horizontal | 4 | 1N5819
5 | J6 | PinHeader_1x02_P2.54mm_Vertical | 1 | Vmaster
6 | J4 | PinHeader_1x35_P2.54mm_Vertical | 1 | comunicacao / sinais digitais
7 | J7 | PinHeader_1x02_P2.54mm_Horizontal | 1 | Eletrodos
8 | U2 | BluePill_STM32F103C | 1 | BluePill_STM32F103C
9 | pullupsda1,pullupscl1 | R_Axial_DIN0207_L6.3mm_D2.5mm_P7.62mm_Horizontal | 2 | 4k7
10 | C3,C1 | CP_Radial_D5.0mm_P2.50mm | 2 | 1 uF
11 | J2 | PinHeader_1x08_P2.54mm_Vertical | 1 | tensoes
12 | J3 | PinHeader_1x27_P2.54mm_Vertical | 1 | sinais analogicos
13 | J5 | PinHeader_1x04_P2.54mm_Horizontal | 1 | sinais_condicionados
14 | U1 | N_8_ADI | 1 | AD828AN
15 | U3 | BluePill_STM32F103C | 1 | BluePill_STM32F103C_master
16 | J1 | PinHeader_1x03_P2.54mm_Vertical | 1 | Vref
17 | C4,C2 | CP_Radial_D5.0mm_P2.50mm | 2 | 470 pF

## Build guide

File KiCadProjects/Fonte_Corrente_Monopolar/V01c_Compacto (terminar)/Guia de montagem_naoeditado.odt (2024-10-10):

Guia de montagem – Circuito impresso

Modelo da placa: Fonte de corrente monopolar compacta versão: 01b

Ljcpcb order: _________________________________

Data: ____/____/____

Separação de material:

- Ferro de solda
- estanho
- fluxo para solda
- alicate de corte
- alicate de bico
- alicate universal
- ventilador de mesa
- papel
- álcool isopropílico
- fita dessoldadora
- sugador de solda
- cotonete
- estilete
- lixa

Separação de componentes

Resistores (designador – quantidade - valor)

R1, R3, R4, R5, R7, R8 – 6 – 100k

R2, R6 – 2 – 1k

R9 – 1 – 220

RganhoINA1 – 1 – 3,3k (pode ser alterado conforme amplitude máx da tensão de entrada)

Rsentinela-I1 – 1 – 10 (ou menor)

Capacitores (designador – quantidade - valor)

C1 – 1 – 1u

C2 – 1 – 470p

Diodos (designador – quantidade - valor)

D1,D2 – 2 – 1N5819

CIs (designador – quantidade - valor)

U1 – 1 – soquete dip8 (ampop duplo)

U2 – 1 – soquete dip8 (INA)

Barra fêmea (designador – quantidade - valor)

J1 – 1 – 05 pinos

Barra macho (designador – quantidade - valor)

J2 – 1 – 03 pinos

J3 – 1 – 07 pinos

Número de placas restantes:

Componentes próximos de acabarem:

Componentes que foram substituídos:

Componentes em falta:

Guia de montagem – Fonte de corrente monopolar V01b - JLCPCB order:______________________ page 1/1

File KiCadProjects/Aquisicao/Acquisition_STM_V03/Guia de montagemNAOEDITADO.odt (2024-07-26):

Guia de montagem – Circuito impresso

Modelo da placa: Placa de aquisição STM32Bluepill versão: 01

Ljcpcb order: _________________________________

Data: ____/____/____

Separação de material:

- Ferro de solda
- estanho
- fluxo para solda
- alicate de corte
- alicate de bico
- alicate universal
- ventilador de mesa
- papel
- álcool isopropílico
- fita dessoldadora
- sugador de solda
- cotonete
- estilete
- lixa

Separação de componentes

Capacitores (designador – quantidade - valor)

C1 – 1 – 680u

C2 – 1 – 220u

C3 – 1 – 10u

C4 – 1 – 33u

Diodos (designador – quantidade - valor)

D1 – 1 – 1N5819

Resistores (designador – quantidade - valor)

R1 – 1 – 510

Indutores (designador – quantidade - valor)

L1 – 1 – 33u

LEDs (designador – quantidade - valor)

L+3.3v1 – 1 – White

CIs (designador – quantidade - valor)

U2 – 1 – LM2596S-5 (step down 5V)

U3 – 1 – LM1117T-3.3 (regulador 3.3V)

Barra pinos reforçados (designador – quantidade - valor)

J1 – 1 – 08 pinos

J2 – 1 – 27 pinos

J3 – 1 – 35 pinos

Barra macho 90º (designador – quantidade - valor)

J4,J5 – 2 – 04 pinos

Microcontrolador (designador – quantidade - valor)

U1,U4,U5,U6 – 4 – stm32 ( 2 barras fêmeas 20 pinos)

Número de placas restantes:

Componentes próximos de acabarem:

Componentes que foram substituídos:

Componentes em falta:

Guia de montagem – Placa de aquisição STM32Bluepill V01 - JLCPCB order:______________________ page 2/2

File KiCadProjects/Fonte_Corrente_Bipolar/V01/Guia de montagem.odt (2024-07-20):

Guia de montagem – Circuito impresso

Modelo da placa: Fonte de corrente bipolar versão: 01

Ljcpcb order: _________________________________

Data: ____/____/____

Separação de material:

- Ferro de solda
- estanho
- fluxo para solda
- alicate de corte
- alicate de bico
- alicate universal
- ventilador de mesa
- papel
- álcool isopropílico
- fita dessoldadora
- sugador de solda
- cotonete
- estilete
- lixa

Separação de componentes

Resistores (designador – quantidade - valor)

R1, R2, R3, R5, R7, R8, R9, R11, R13, R14, R16, R17– 12 – 100k

R4, R6, R10, R12 – 4 – 1k

R19, R20 – 2 – 1,5k

R21 – 1 – 470

R22 – 1 – 510

R15, R18 – 2 – 220

Rganho-I1,Rganho-I2 – 2 – 3,3k

RpSCLx, RpSDAx – 8 – 4,7k

Rsentinela-I1,Rsentinela-I2 – 2 - 10

diodos (designador – quantidade - valor)

D1,D2,D3,D4 – 4 – 1N5819

Capacitores (designador – quantidade - valor)

C1,C3 – 2 – 1u

C2,C4 – 2 – 470p

LEDs (designador – quantidade - valor)

L+3.3v1 – 1 – Yelow

L+5v1 – 1 – Green

L+9v1 – 1 – Blue

L-9v1 – 1 – Red

CIs (designador – quantidade - valor)

U1,U3 – 2 – dip8(ampop duplo)

U1-INA-I1, U2-INA-I2 – 2 – INA128

Barra pinos reforçados (designador – quantidade - valor)

J1 – 1 – 08 pinos

J2 – 1 – 27 pinos

J3 – 1 – 35 pinos

Barra macho (designador – quantidade - valor)

J4,J5,J7 – 3 – 03 pinos

Número de placas restantes:

Componentes próximos de acabarem:

Componentes que foram substituídos:

Componentes em falta:

Guia de montagem – Fonte de corrente bipolar V01 - JLCPCB order:______________________ page 2/2

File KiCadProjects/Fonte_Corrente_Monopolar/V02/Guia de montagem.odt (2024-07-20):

Guia de montagem – Circuito impresso

Modelo da placa: Fonte de corrente monopolar versão: 02

Ljcpcb order: _________________________________

Data: ____/____/____

Separação de material:

- Ferro de solda
- estanho
- fluxo para solda
- alicate de corte
- alicate de bico
- alicate universal
- ventilador de mesa
- papel
- álcool isopropílico
- fita dessoldadora
- sugador de solda
- cotonete
- estilete
- lixa

Separação de componentes

Resistores (designador – quantidade - valor)

R1, R2, R3, R5, R10, R11 – 6 – 100k

R4, R6 – 2 – 1k

R7, R13 – 2 – 1,5k

R8 – 1 – 470

R9 – 1 – 510

R12 – 1 – 220

Rganho-I1 – 1 – 3,3k

RpSCLx, RpSDAx – 8 – 4,7k

Rsentinela-I1 – 1 - 10

diodos (designador – quantidade - valor)

D1,D2 – 2 – 1N5819

Capacitores (designador – quantidade - valor)

C3 – 1 – 1u

C4 – 1 – 470p

LEDs (designador – quantidade - valor)

L+3.3v1 – 1 – Yelow

L+5v1 – 1 – Green

L+9v1 – 1 – Blue

L-9v1 – 1 – Red

CIs (designador – quantidade - valor)

U1,U3 – 2 – dip8(ampop duplo)

U2 – 1 – INA-I1

Barra pinos reforçados (designador – quantidade - valor)

J1 – 1 – 08 pinos

J2 – 1 – 27 pinos

J3 – 1 – 35 pinos

Barra macho (designador – quantidade - valor)

J4,J7 – 2 – 03 pinos

Número de placas restantes:

Componentes próximos de acabarem:

Componentes que foram substituídos:

Componentes em falta:

Guia de montagem – Fonte de corrente monopolar V02 - JLCPCB order:______________________ page 2/2

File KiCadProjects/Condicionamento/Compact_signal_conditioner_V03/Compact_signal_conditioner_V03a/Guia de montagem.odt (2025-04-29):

Guia de montagem – Circuito impresso

Modelo da placa: Condicionamento compacto versão: 03a

Ljcpcb order: _________________________________

Data: ____/____/____

Separação de material:

- Ferro de solda
- estanho
- fluxo para solda
- alicate de corte
- alicate de bico
- alicate universal
- ventilador de mesa
- papel
- álcool isopropílico
- fita dessoldadora
- sugador de solda
- cotonete
- estilete
- lixa

Separação de componentes

Resistores (designador – quantidade - valor)

R1, R8 – 2 – 220

R2,R3,R4,R5 – 4 – 100k

Rfg_1,Rfg_2 – 2 - 51k

RC1,RC2,RC3,RC4,RC5,RC6,RC7,RC8,RC9,RC10 – 10 – aberto.

Capacitores (designador – quantidade - valor)

C1,C4 – 2 – 470p

C2,C3 – 2 – 1u

Diodos (designador – quantidade - valor)

D1,D2,D3,D4 – 4 – 1N5819

CIs (designador – quantidade - valor)

U1, U2 – 2 – soquete 14 (chaves)

U1-buffer1,U2-gain1,U3-Cond-DIP1 – 3 – soquete 8 (AmpOp)

Barra macho 90º (designador – quantidade - valor)

J2 – 1 – 02 pinos

J8 – 1 – 06 pinos

Barra fêmea 90º (designador – quantidade - valor)

J5 – 1 – 06 pinos

Barra macho (designador – quantidade - valor)

J6,J7 – 2 – 03 pinos

Barra dupla macho 90º (designador – quantidade - valor)

J1 – 1 – 2x09 pinos

Número de placas restantes:

Componentes próximos de acabarem:

Componentes que foram substituídos:

Componentes em falta:

Guia de montagem – Condicionamento compacto V03a - JLCPCB order:______________________ page 1/1

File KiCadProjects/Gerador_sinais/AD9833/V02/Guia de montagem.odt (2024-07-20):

Guia de montagem – Circuito impresso

Modelo da placa: Gerador de sinais AD9833 versão: 02

Ljcpcb order: _________________________________

Data: ____/____/____

Separação de material:

- Ferro de solda
- estanho
- fluxo para solda
- alicate de corte
- alicate de bico
- alicate universal
- ventilador de mesa
- papel
- álcool isopropílico
- fita dessoldadora
- sugador de solda
- cotonete
- estilete
- lixa

Separação de componentes

Resistores (designador – quantidade - valor)

R1,R9 – 2 – 160k

R2 – 1 – 10k

R3,R4 – 2 – 1,5k

R5 – 1 – 470

R6 – 1 – 510

Capacitores (designador – quantidade - valor)

C1,C2 – 2 – 100n

LEDs (designador – quantidade - valor)

L+3.3v1 – 1 – Yelow

L+5v1 – 1 – Green

L+9v1 – 1 – Blue

L-9v1 – 1 – Red

CIs (designador – quantidade - valor)

U1 – 1 – dip8(ampop duplo)

U2 – 1 – x9C10x module (necessário barra fêmea – 2 – 5 pinos)

U3 – 1 – AD9833 module (necessário barra fêmea – 1 – 7 pinos)

Barra pinos reforçados (designador – quantidade - valor)

J1 – 1 – 08 pinos

J2 – 1 – 27 pinos

J3 – 1 – 35 pinos

Barra fêmea (designador – quantidade - valor)

*J6 – 1 – 05 pinos (fixado na placa do encoder)

Barra macho 90º (designador – quantidade - valor)

J4 – 1 – 06 pinos

J6 – 1 – 05 pinos (para fixação do encoder)

Barra macho (designador – quantidade - valor)

J5 – 1 – 03 pinos

Microcontrolador (designador – quantidade - valor)

A1 – 1 – arduino nano ( 2 barras fêmeas 15 pinos)

Número de placas restantes:

Componentes próximos de acabarem:

Componentes que foram substituídos:

Componentes em falta:

Guia de montagem – Gerador de sinais AD9833 V02 - JLCPCB order:______________________ page 1/2

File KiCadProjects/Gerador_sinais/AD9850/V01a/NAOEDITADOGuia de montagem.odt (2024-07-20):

Guia de montagem – Circuito impresso

Modelo da placa: Gerador de sinais AD9850 versão: 01

Ljcpcb order: _________________________________

Data: ____/____/____

Separação de material:

- Ferro de solda
- estanho
- fluxo para solda
- alicate de corte
- alicate de bico
- alicate universal
- ventilador de mesa
- papel
- álcool isopropílico
- fita dessoldadora
- sugador de solda
- cotonete
- estilete
- lixa

Separação de componentes

Resistores (designador – quantidade - valor)

R1,R2 – 2 – 1,5k

R3 – 1 – 470

R4 – 1 – 510

R5,R6 – 2 – 51k

R7,R8 – 2 – 4,7k

R9,R10,R11,R12,R13,R14 – 6 - 160k

Capacitores (designador – quantidade - valor)

C1, C2, C3, C4, C5, C6 – 6 – 100n

LEDs (designador – quantidade - valor)

L+3.3v1 – 1 – Yelow

L+5v1 – 1 – Green

L+9v1 – 1 – Blue

L-9v1 – 1 – Red

CIs (designador – quantidade - valor)

U1 – 1 – AD9850 module (necessário barra fêmea - 2 – 10 pinos)

U3,U6,U7 – 3 – dip8(ampop duplo)

U4,U5 – 2 – x9C10x module (necessário barra fêmea – 2 – 5 pinos)

Barra pinos reforçados (designador – quantidade - valor)

J1 – 1 – 08 pinos

J2 – 1 – 27 pinos

J3 – 1 – 35 pinos

Barra fêmea (designador – quantidade - valor)

*J9 – 1 – 05 pinos (fixado na placa do encoder)

Barra macho (designador – quantidade - valor)

J4,J5 – 2 – 02 pinos

J6,J7 – 2 – 03 pinos

Barra macho 90º (designador – quantidade - valor)

J8 – 1 – 03 pinos

J9 – 1 – 05 pinos (para fixação do encoder)

J10 – 1 – 08 pinos

J11 – 1 – 05 pinos

Microcontrolador (designador – quantidade - valor)

U2 – 1 – stm32 ( 2 barras fêmeas 20 pinos)

Número de placas restantes:

Componentes próximos de acabarem:

Componentes que foram substituídos:

Componentes em falta:

Guia de montagem – Gerador de sinais AD9850 V01 - JLCPCB order:______________________ page 2/2

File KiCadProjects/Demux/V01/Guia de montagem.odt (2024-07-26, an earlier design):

Guia de montagem – Circuito impresso

Modelo da placa: Demux versão: 02

Ljcpcb order: _________________________________

Data: ____/____/____

Separação de material:

- Ferro de solda
- estanho
- fluxo para solda
- alicate de corte
- alicate de bico
- alicate universal
- ventilador de mesa
- papel
- álcool isopropílico
- fita dessoldadora
- sugador de solda
- cotonete
- estilete
- lixa

Separação de componentes

Resistores (designador – quantidade - valor)

R1, R2 – 2 – 1,5k

R3 – 1 – 470

R4 – 1 – 510

Barra pinos reforçados (designador – quantidade - valor)

J1 – 1 – 08 pinos

J2 – 1 – 27 pinos

J3 – 1 – 35 pinos

CIs (designador – quantidade - valor)

UxAx, UxBx – 10 – dip16(multiplexador de 8 canais)

LEDs (designador – quantidade - valor)

L+3.3v1 – 1 – Yelow

L+5v1 – 1 – Green

L+9v1 – 1 – Blue

L-9v1 – 1 – Red

Barra macho dupla 90º (designador – quantidade - valor)

J14,J15 – 2 – 12 pinos (24 total)

Barra macho (designador – quantidade - valor)

J4 – 1 – 03 pinos

J5,J6,J7,…,J13 – 9 – 02 pinos

Microcontrolador (designador – quantidade - valor)

U2 – 1 – stm32 ( 2 barras fêmeas 20 pinos)

Número de placas restantes:

Componentes próximos de acabarem:

Componentes que foram substituídos:

Componentes em falta:

Guia de montagem – Demux V02 - JLCPCB order:______________________ page 2/2

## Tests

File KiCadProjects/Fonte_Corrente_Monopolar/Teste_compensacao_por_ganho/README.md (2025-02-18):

Testes de compensação da fonte de corrente por meio de ganho aplicado ao sinal de entrada.

Estes testes fazem parte do artigo submetido ao CBEB 2024.

Pasta "Tensao_sobre_carga": Considera para cálculo da corrente a tensão vista sobre a carga (não utilizados nos trabalhos).

Pasta "Tensao_INA":  Considera para cálculo da corrente a tensão vista a saída do INA (resultados considerados no artigo e na dissertação.

    - Medições considerando apenas carga resistiva:
        500 ohm com e sem ganho
    - Medições considerando  carga RC paralelo:
        500 ohm // 1.8pF com e sem ganho
        500 ohm //100nF com e sem ganho
    
    - Pasta "Gráficos":
        resposta em frequenciada corrente para cada um dos cenários individualmente
        "Resultados_agrupados" Resposta em frequencia da corrente para todos os cenarios agrupados (apresentado no trabalho).
        "tensao_saida" Resposta em frequencia da tensao de saida do INA para todos os cenarios agrupados

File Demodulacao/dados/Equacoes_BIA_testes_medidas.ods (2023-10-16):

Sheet: equacoes
Kyle part i (2004) |  |  | altura [cm] | peso [kg] | circunferência cm]
FFM – Massa magra
equação | ID equação | frequência | parâmetros elétricos | parâmetros corporais | publico | fonte | erro (SEE) [kg] | r²
-4,104 + 0,518*Ht²/R + ,0231*p + 0,130*X + 4,229 * s | FFM_eq1 | 50 kHz | R = resistência; X = reatância | Ht = altura; p = peso; s = sexo [1 = homem 0 = mulher] | Adultos 18-94 anos | kyle et al (2001) | 1,8 | 0,97
5,49 + 0,476 * Ht²/R + 0,295 * p | FFM_eq2 | 50 kHz | R = resistência | Ht = altura; p = peso | Mulheres 18-29 anos | Lohman (1992) | 2,1 | ---
11,59 + 0,493 * Ht²/R + 0,141 * p | FFM_eq3 | 50 kHz | R = resistência | Ht = altura; p = peso | Mulheres 30-49 anos | Lohman (1992) | 2,5 | ---
5,32 + 0,485 * Ht²/R + 0,338 * p | FFM_eq4 | 50 kHz | R = resistência | Ht = altura; p = peso | Homens 18-29 anos | Lohman (1992) | 2,9 | ---
4,51 + 0,549 * Ht²/R + 0,163 * p + 0,092*X | FFM_eq5 | 50 kHz | R = resistência; X = reatância | Ht = altura; p = peso | Homens 30-49 anos | Lohman (1992) | 3,2 | ---
-12,44 + 0,34*Ht²/R + 0,1534 *Ht + 0,273 * p - 0,127*a + 4,56*s | FFM_eq6 | 50 kHz | R = resistência | Ht = altura; p = peso; s = sexo [1 = homem 0 = mulher]; a = idade | Adultos >16 anos | Deurenberg et al (1991) | 2,6 | 0,93
6,37 + 0,64 * p + 0,40*Ht²/Z – 0,16*a – 2,71 * s | FFM_eq7 | 1 MHz | Z = impedância | Ht = altura; p = peso; s = sexo [1 = homem 2 = mulher]; a = idade | Adultos 12-71 anos | Boulier et al (1990) | 2,6 | 0,92
 | FFM_eq8 | 50 kHz | Z = impedância | parâmetros etnicos |  | Kotler (1996) | 6,56% | 0,71
20,05 – 0,04904*R +0,001254*Ht² + 0,1555*p + 0,1417*X – 0,0833*a | FFM_eq9 | 50 kHz | R = resistência; X = reatância | Ht = altura; p = peso; a = idade | Mulheres 18-60 anos | Stolarczyk et al (1994) | 2,6 | 0,75
-9,529 + 0,696*Ht²/R + 0,168*p + 0,016*R | FFM_eq10 | 50 kHz | R = resistência; X = reatância | Ht = altura; p = peso; a = idade | Mulheres 12-94 anos | Sun(2003) | 2,9 | 0,83
-10,678 + 0,652*Ht²/R + 0,262*p +0,015*R | FFM_eq11 | 50 kHz | R = resistência | Ht = altura; p = peso | Homens 12-94 anos | Sun (2003) | 3,9 | 0,9
2,68 + 0,2*ht²/R + 0,19*p + 2,55*e + 0,1157*Ht | FFM_eq12 | 50 kHz | R = resistência | Ht = altura; p = peso; e = [0 = caucasiano 1 = Afroamericano] | Homens (???) obesos 25-45 anos | Jakicic (1998) | 8,8 | 0,65
2,04 + 0,02*Ht²/R = 0,19*p +2,63*e +0,2583*Ht | FFM_eq13 | 50 kHz | R = resistência | Ht = altura; p = peso; e = [0 = caucasiano 1 = Afroamericano] | Mulheres(???) obesas 15-45 anos | Jakicic (1998) | 8,8 | 0,65
BF/FM – Gordura
equação | ID equação | frequência | parâmetros elétricos | parâmetros corporais | publico | fonte | erro (SEE) [kg]
(%) : -23,58 + 20,03 * R * p / Ht² + 0,29 * tc -4,99 * s + 0,52 * ac | FM_eq1 | 50 kHz | R = resistência | Ht = altura; p = peso; s = sexo [1 = homem 0 = mulher]; Tc = circunferência seg.coxa; ac = circunferência seg.braço | Idosos 65-94 anos | Baumgartner et al (1991) | 3,80% | 0,73
14,94 – 0,079 Ht² /R + 0,818 * p – 0,231*Ht – 0,064*s*p + 0,077*a | FM_eq2 | 50 kHz | R = resistência | Ht = altura; p = peso; s = sexo [1 = homem 0 = mulher]; a = idade | Adultos 35-65 anos | Heitmann (1990) | 3,6 | 0,9
-5,9150 + 0,7395*p -0,3327*Ht +0,0846*a + 0,048*up*R +0,2705*t*R + 0,0384*ll*R – 0,1219*ll*X | FM_eq3 | 50 kHz | R = resistência; X = reatância | Ht = altura; p = peso; a = idade; Up = membro superior; ll = membro inferior; t = tronco | Mulheres 21-64 anos | Organ et al (1994) | 1,9 | 0,93
-4,2422 + 0,7368*p -0,0482*Ht +0,1170*a + 0,0393*up*R + 0,5110*t*R + 0,0654*ll*R – 0,2560*ll*X | FM_eq4 | 50 kHz | R = resistência; X = reatância | Ht = altura; p = peso; a = idade; Up = membro superior; ll = membro inferior; t = tronco | Homens 21-64 anos | Organ et al (1994) | 2,8 | 0,93
TBW – Total body water
equação |  | frequência | parâmetros elétricos | parâmetros corporais | publico | fonte | erro (SEE) [kg]
6,69 + 0,34573*Ht² / Z + 0,17065*p – 0,11*a + 2,66*s |  | 100 kHz | Z = impedância | Ht = altura; p = peso; s = sexo [1 = homem 0 = mulher]; a = idade | Adultos | Deurenberg et al (1995) | 1,73 | 0,95
6,53 + 0,36740*Ht² / Z + 0,17531*p – 0,11*a + 2,83*s |  | 50 kHz | Z = impedância | Ht = altura; p = peso; s = sexo [1 = homem 0 = mulher]; a = idade | Adultos | Deurenberg et al (1995) | 1,73 | 0,95
0,6 + 0,50*Ht² / R + 0,186*p |  | 0 Hz | R = resistência | Ht = altura; p = peso | Adultos | Cornish et al (1996) | 2,1
-17,58 + 0,240*Ht² / R - 0,172*p + 0,040*s*p + 0,165*Ht |  | 50 kHz | R = resistência | Ht = altura; p = peso; s = sexo [1 = homem 0 = mulher] | Adultos 35-65 anos | Heitmann (1990) | 3,47
2,896 + 0,366*Ht²/R + 0,137*p + 2,485*s |  | 100 kHz | R = resistência | Ht = altura; p = peso; s = sexo [1 = homem 0 = mulher] | Idosos | Vache et al (1998) | 1,3
14,0107 + 0,29753*Ht² / R + 0,14739*p – 3,63734*s – 0,07299*a |  | 224 kHz | R = resistência | Ht = altura; p = peso; s = sexo [1 = homem 0 = mulher]; a = idade | Adultos 19-65 anos | Van Loan and Mayclin (1992) | 3,1
 |  |  |  | 5
ECW – água extracelular
equação |  | frequência | parâmetros elétricos | parâmetros corporais | publico | fonte | erro (SEE) [kg]
2,30 + 0,19528*Ht² /Z + 0,06987*p – 0,02*a |  | 1 kHz | Z = impedância | Ht = altura; p = peso; a = idade | Adultos | Deurenberg et al (1995) | 0,98
2,53 + 0,18903*Ht² /Z + 0,06753*p – 0,02*a |  | 5 kHz | Z = impedância | Ht = altura; p = peso; a = idade | Adultos | Deurenberg et al (1995) | 1,02
-5,17753 + 0,09989*Ht² / R + 0,09322*p - 1,3962*s |  | 224 kHz | R = resistência | Ht = altura; p = peso; s = sexo [1 = homem 0 = mulher] | Adultos 16-65 anos | Van Loan and Mayclin (1992) | 1,06
-5,22 + 0,2*Ht²/R + 0,005*Ht²/X + 0,08*p + 1,9 + 1,86*s |  | 50 kHz | R = resistência; X = reatância | Ht = altura; p = peso; s = sexo [0 = homem 1 = mulher] | Adultos | Sergi (1993) | 1,75 | 0,89

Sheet: Calculo FFM
Voluntário 1 – Gustavo
R – resistencia | X – reatancia |  | Ht – altura [cm] | P – peso [kg] | S – sexo [1-h 0-m] | A – anos | FFM_eq1 |  | FFM_eq2 |  | FFM_eq3 |  | FFM_eq4 |  | FFM_eq5 |  | FFM_eq6 |  | omron Fat (%) | omron FFM (%) | diff eq1 (%) | diff eq2 (%) | diff eq3 (%) | diff eq4 (%) | diff eq5 (%) | diff eq6 (%) | adequado ao Voluntario
431,14 | 369,28 |  | 178,00 | 72,80 | 1,00 | 26,00 | (kg) | (%) | (kg) | (%) | (kg) | (%) | (kg) | (%) | (kg) | (%) | (kg) | (%) | 22,60 | 77,40 | 48,87 | 6,85 | -0,11 | 13,22 | 54,76 | 6,02 | adequado ao Voluntario (considera reatancia)
457,04 | 214,92 |  |  |  |  |  | 83,89 | 115,23 | 60,21 | 82,70 | 56,28 | 77,31 | 63,80 | 87,63 | 87,20 | 119,78 | 59,74 | 82,06
484,43 | 481,98
467,87 | 354,34
428,01 | 345,07
453,70 | 353,12 |  | média
Voluntário 2 – Silvio
R – resistencia | X – reatancia |  | Ht – altura [cm] | P – peso [kg] | S – sexo [1-h 0-m] | A – anos | FFM_eq1 |  | FFM_eq2 |  | FFM_eq3 |  | FFM_eq4 |  | FFM_eq5 |  | FFM_eq6 |  | omron Fat (%) | omron FFM (%) | diff eq1 (%) | diff eq2 (%) | diff eq3 (%) | diff eq4 (%) | diff eq5 (%) | diff eq6 (%)
309,29 | 12,01 |  | 166,00 | 74,80 | 1,00 | 33,00 | (kg) | (%) | (kg) | (%) | (kg) | (%) | (kg) | (%) | (kg) | (%) | (kg) | (%) | 32,90 | 67,10 | 14,42 | 35,07 | 27,13 | 42,65 | 42,36 | 24,63
304,76 | 151,64 |  |  |  |  |  | 57,43 | 76,78 | 67,79 | 90,63 | 63,81 | 85,31 | 71,60 | 95,72 | 71,45 | 95,53 | 62,55 | 83,63
319,49 | 138,78
362,55 | 82,88
348,90 | 130,60
311,01 | 28,33
326,00 | 90,71 |  | média
Voluntário
Voluntário 1 – Gustavo
R – resistencia | X – reatancia | Z – impedancia | Ht – altura [cm] | P – peso [kg] | S – sexo [1-h 0-m] | A – anos | FFM_eq1 (adultos) |  | FFM_eq2 (Mulheres 18-29 anos) |  | FFM_eq3 (Mulheres 30-49 anos) |  | FFM_eq4 (Homens 18-29 anos) |  | FFM_eq5 (Homens 30-49 anos) |  | FFM_eq6 (Adultos >16 anos) |  | omron Fat (%) | omron FFM (%) | diff eq1 (%) | diff eq2 (%) | diff eq3 (%) | diff eq4 (%) | diff eq5 (%) | diff eq6 (%) | adequado ao Voluntario
548,38 | 56,93 | 542,24 | 178,00 | 74,80 | 1,00 | 27,00 | (kg) | (%) | (kg) | (%) | (kg) | (%) | (kg) | (%) | (kg) | (%) | (kg) | (%) | 24,80 | 75,20 | -30,21 | -2,29 | -10,18 | 4,05 | -4,58 | -0,46 | adequado ao Voluntario (considera reatancia)
551,98 | 58,82 | 546,14 |  |  |  |  | 39,26 | 52,48 | 54,96 | 73,48 | 50,52 | 67,54 | 58,53 | 78,24 | 53,68 | 71,76 | 55,99 | 74,86
549,85 | 58,23 | 544,06
548,35 | 58,19 | 542,55
550,33 | 59,26 | 544,66
552,67 | 62,07 | 547,42
551,29 | 56,44 | 545,05
549,46 | 60,15 | 543,86
550,85 | 56,08 | 544,6
549,84 | 56,9 | 543,88
550,3 | 58,307 | 544,446 | média
vis fat | peso | imc | body fat | muscle | rm | body age
6,00 | 74,80 | 23,60 | 24,80 | 36,10 | 1680kcal | 39,00
Voluntário 2 – Silvio
R – resistencia | X – reatancia | Z – impedancia | Ht – altura [cm] | P – peso [kg] | S – sexo [1-h 0-m] | A – anos | FFM_eq1 (adultos) |  | FFM_eq2 (Mulheres 18-29 anos) |  | FFM_eq3 (Mulheres 30-49 anos) |  | FFM_eq4 (Homens 18-29 anos) |  | FFM_eq5 (Homens 30-49 anos) |  | FFM_eq6 (Adultos >16 anos) |  | omron Fat (%) | omron FFM (%) | diff eq1 (%) | diff eq2 (%) | diff eq3 (%) | diff eq4 (%) | diff eq5 (%) | diff eq6 (%)
399,54 | 40,58 | 389,96 | 166,00 | 75,70 | 1,00 | 34,00 | (kg) | (%) | (kg) | (%) | (kg) | (%) | (kg) | (%) | (kg) | (%) | (kg) | (%) | 26,50 | 73,50 | -24,77 | 6,35 | -1,36 | 12,86 | 2,53 | 0,66
401,2 | 41,2 | 391,76 |  |  |  |  | 42,82 | 56,57 | 60,54 | 79,98 | 56,15 | 74,18 | 64,25 | 84,87 | 58,37 | 77,10 | 57,30 | 75,70
402,24 | 40,91 | 392,74
400,63 | 41,23 | 391,14
403,32 | 40,12 | 393,54
400,25 | 41,17 | 390,81
401,36 | 42,78 | 392,18
398,67 | 41,6 | 389,35
399,38 | 40,13 | 389,74
402,13 | 41,24 | 392,7
400,872 | 41,096 | 391,392 | média
vis fat | peso | imc | body fat | muscle | rm | body age
11,00 | 75,70 | 27,50 | 26,50 | 36,20 | 1.715,00 | 42,00

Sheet: calculo FM
Voluntário 1 – Gustavo
R – resistencia | X – reatancia | Ht – altura [cm] | P – peso [kg] | S – sexo | A – anos | FM_eq1 |  | FM_eq2 |  | FM_eq3 |  | FM_eq4 |  | omron Fat (%) | diff eq1 (%) | diff eq2 (%) | diff eq3 (%) | diff eq4 (%) | diff(%) (FM= weight - FFM eq6) | adequado ao Voluntario
431,14 | 369,28 | 178,00 | 72,80 | 1,00 | 26,00 | (kg) | (%) | (kg) | (%) | (kg) | (%) | (kg) | (%) | 22,60 |  | 53,15 |  |  | -20,63 | adequado ao Voluntario (considera reatancia)
457,04 | 214,92 |  |  |  |  |  |  | 25,20 | 34,61
484,43 | 481,98
467,87 | 354,34
428,01 | 345,07
453,70 | 353,12 | média
Voluntário 2 – Silvio
R – resistencia | X – reatancia | Ht – altura [cm] | P – peso [kg] | S – sexo | A – anos | FM_eq1 |  | FM_eq2 |  | FM_eq3 |  | FM_eq4 |  | omron Fat (%) | diff eq1 (%) | diff eq2 (%) | diff eq3 (%) | diff eq4 (%) | diff(%) (FM= weight - FFM eq6)
309,29 | 12,01 | 166,00 | 74,80 | 1,00 | 33,00 | (kg) | (%) | (kg) | (%) | (kg) | (%) | (kg) | (%) | 32,90 |  | 24,90 |  |  | -50,23
304,76 | 151,64 |  |  |  |  |  |  | 30,74 | 41,09
319,49 | 138,78
362,55 | 82,88
348,90 | 130,60
311,01 | 28,33
326,00 | 90,71 | média

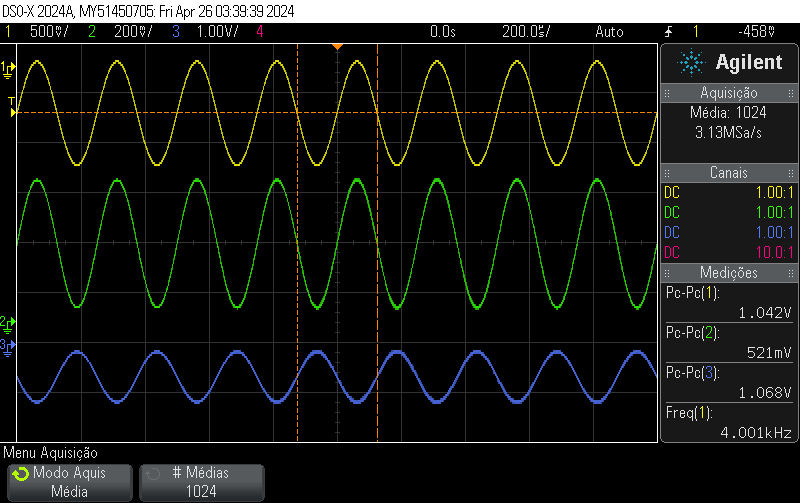
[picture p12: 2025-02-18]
KiCadProjects/Fonte_Corrente_Monopolar/Teste_compensacao_por_ganho/Tensao_sobre_carga/cargaR_500_ganho/scope_171.png

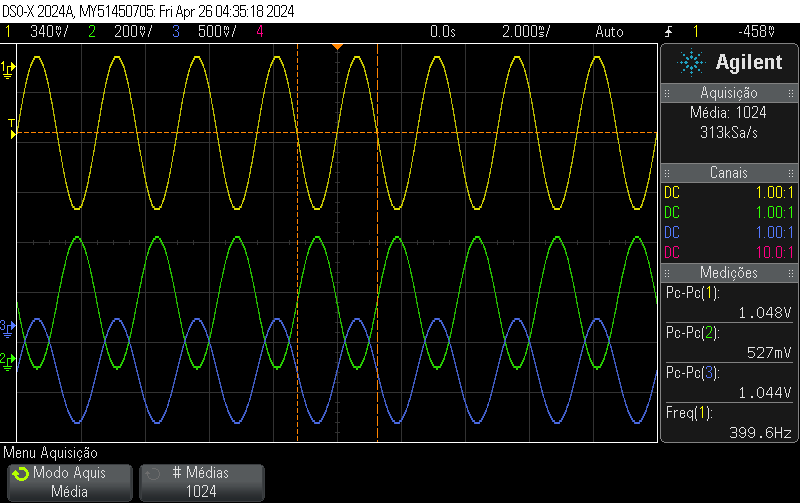
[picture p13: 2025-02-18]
KiCadProjects/Fonte_Corrente_Monopolar/Teste_compensacao_por_ganho/Tensao_sobre_carga/cargaRC_500_1_8p_semganho/scope_276.png

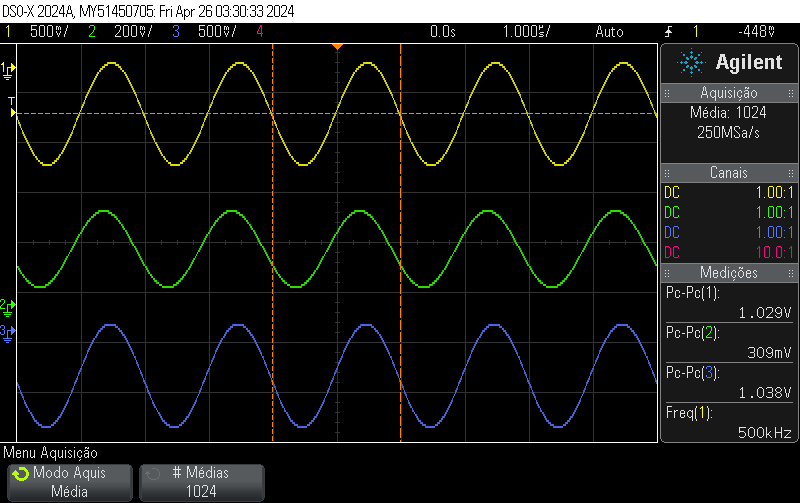
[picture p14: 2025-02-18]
KiCadProjects/Fonte_Corrente_Monopolar/Teste_compensacao_por_ganho/Tensao_sobre_carga/cargaR_500_semganho/scope_153.png

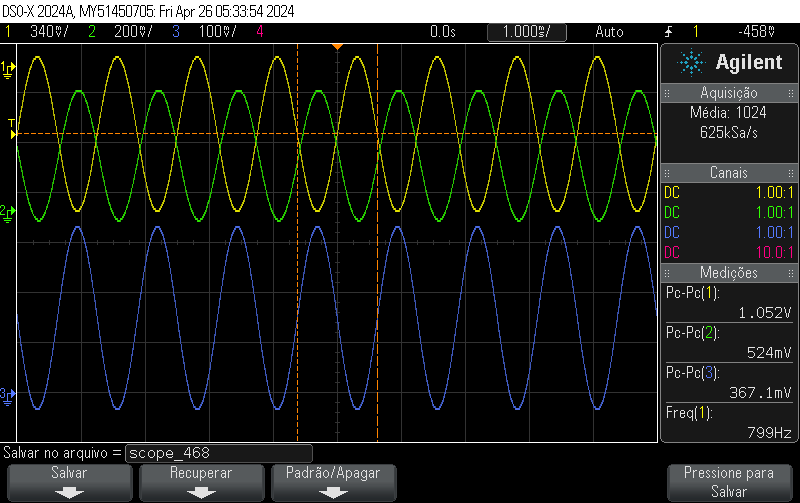
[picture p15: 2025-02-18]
KiCadProjects/Fonte_Corrente_Monopolar/Teste_compensacao_por_ganho/Tensao_INA/cargaRC_500_100n_semganho/scope_468.png

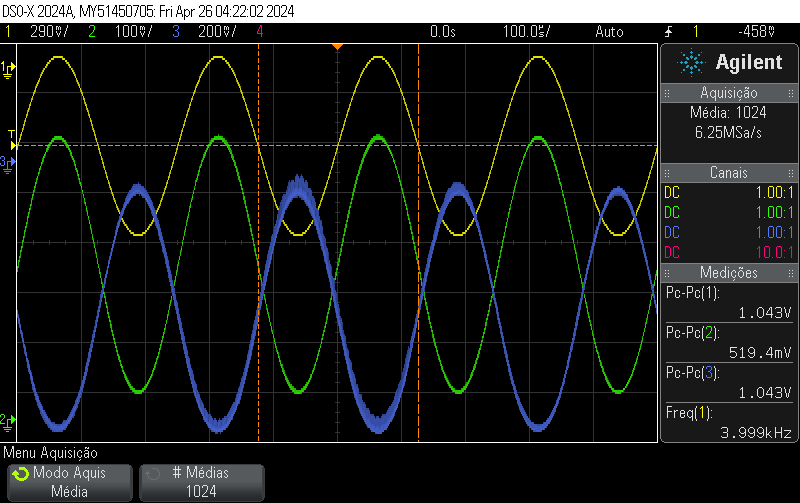
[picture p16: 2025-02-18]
KiCadProjects/Fonte_Corrente_Monopolar/Teste_compensacao_por_ganho/Tensao_sobre_carga/cargaRC_500_1_8p_ganho/scope_247.png

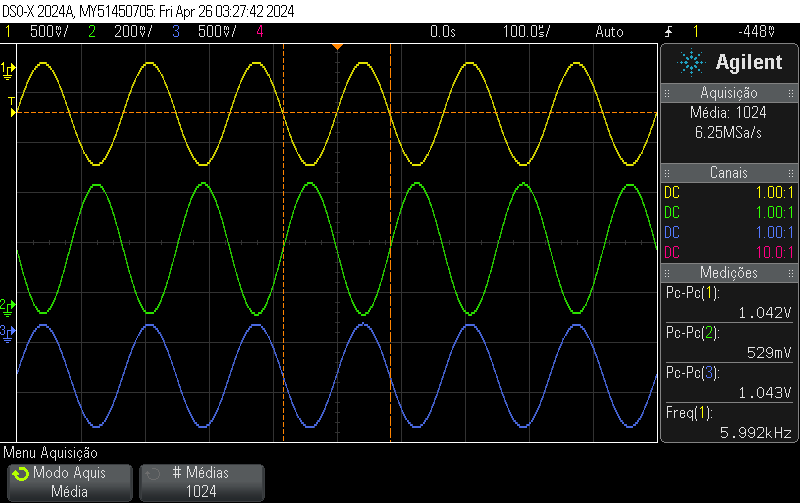
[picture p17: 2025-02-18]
KiCadProjects/Fonte_Corrente_Monopolar/Teste_compensacao_por_ganho/Tensao_sobre_carga/cargaR_500_semganho/scope_136.png

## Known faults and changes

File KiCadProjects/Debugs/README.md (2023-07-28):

# Debugs Placas EITduino

-----------------------------------------------------------------------------------------------------------------------------------------------

## gerador de sinais

- Canal 3 (azul): sinal de saída do gerador de sinais
 
- Canal 4 (vermelho): sinal de alimentação na entrada da placa do Gerador de sinais. Alimentação do arduino UNO

#### Modo de aquisição normal

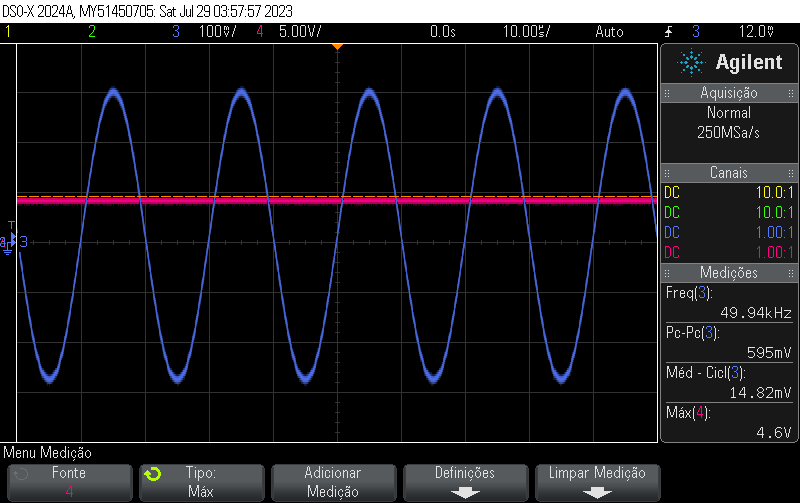
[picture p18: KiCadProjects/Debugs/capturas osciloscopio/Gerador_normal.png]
Captura Gerador de sinais - normal


#### Modo de aquisição média n1024

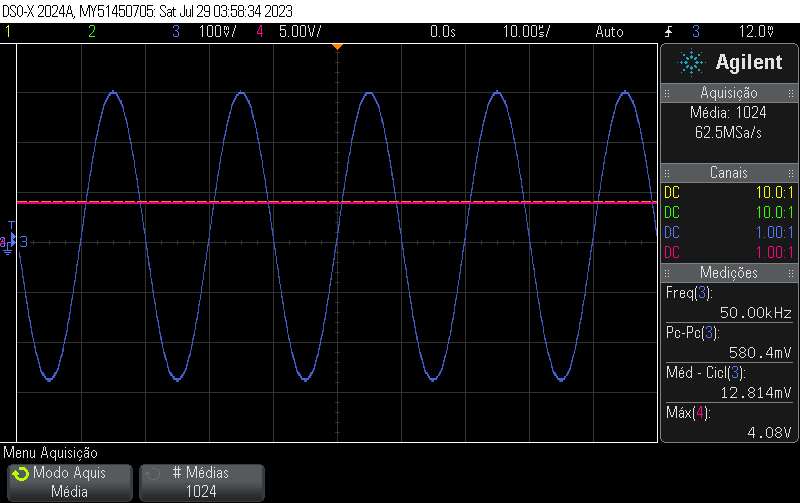
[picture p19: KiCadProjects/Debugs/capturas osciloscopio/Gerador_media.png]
Captura Gerador de sinais - media


-----------------------------------------------------------------------------------------------------------------------------------------------

## Fonte de corrente

- Canal 3 (azul): sinal de saída do gerador de sinais
 
- Canal 4 (vermelho): Saída do INA

#### Modo de aquisição normal

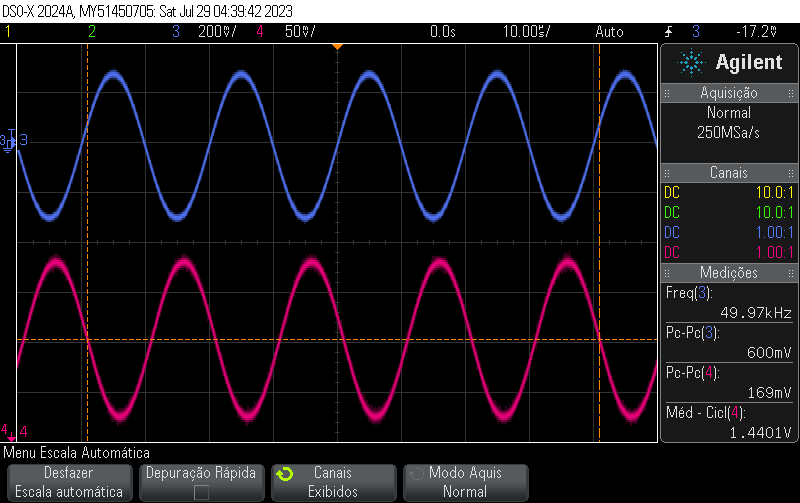
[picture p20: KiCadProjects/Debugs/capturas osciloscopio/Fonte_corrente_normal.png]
Captura fonte de corrente - normal


#### Modo de aquisição média n1024

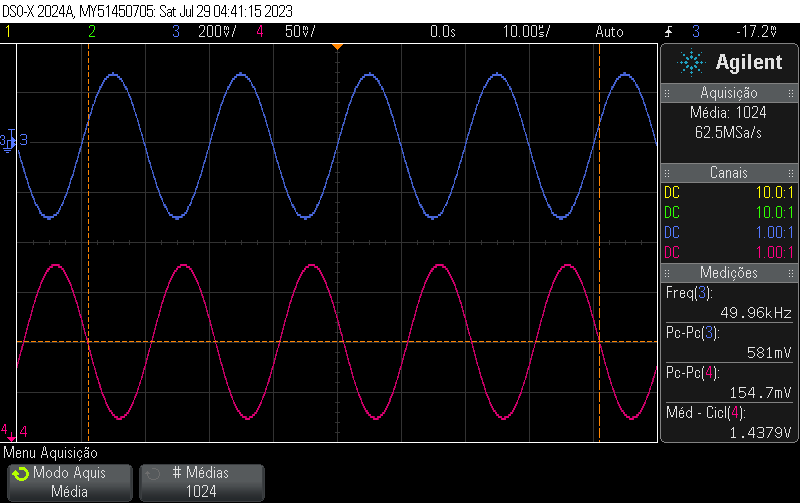
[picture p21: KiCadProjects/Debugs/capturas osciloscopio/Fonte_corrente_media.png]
Captura fonte de corrente - media


-----------------------------------------------------------------------------------------------------------------------------------------------

## Aquisição uC

- Canal 3 (azul): Saída do INA da fonte de corrente
 
- Canal 4 (vermelho): Entrada do INA nos ADCS dos uC

#### Modo de aquisição normal

O sinal está sofrendo deslocamento, talvez por efeito capacitivo entre as trilhas(?)
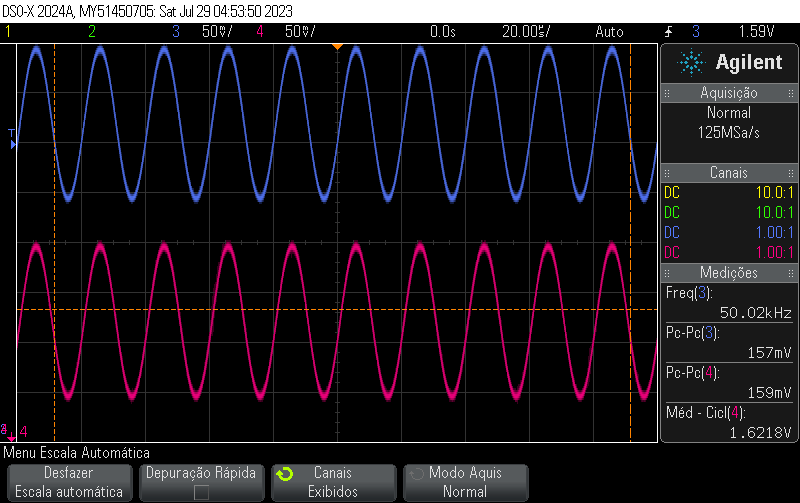
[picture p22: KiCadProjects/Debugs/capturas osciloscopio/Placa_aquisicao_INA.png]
Captura placa de aquisicao - sinal do INA - normal


<Captura Gerador de sinais - normal>

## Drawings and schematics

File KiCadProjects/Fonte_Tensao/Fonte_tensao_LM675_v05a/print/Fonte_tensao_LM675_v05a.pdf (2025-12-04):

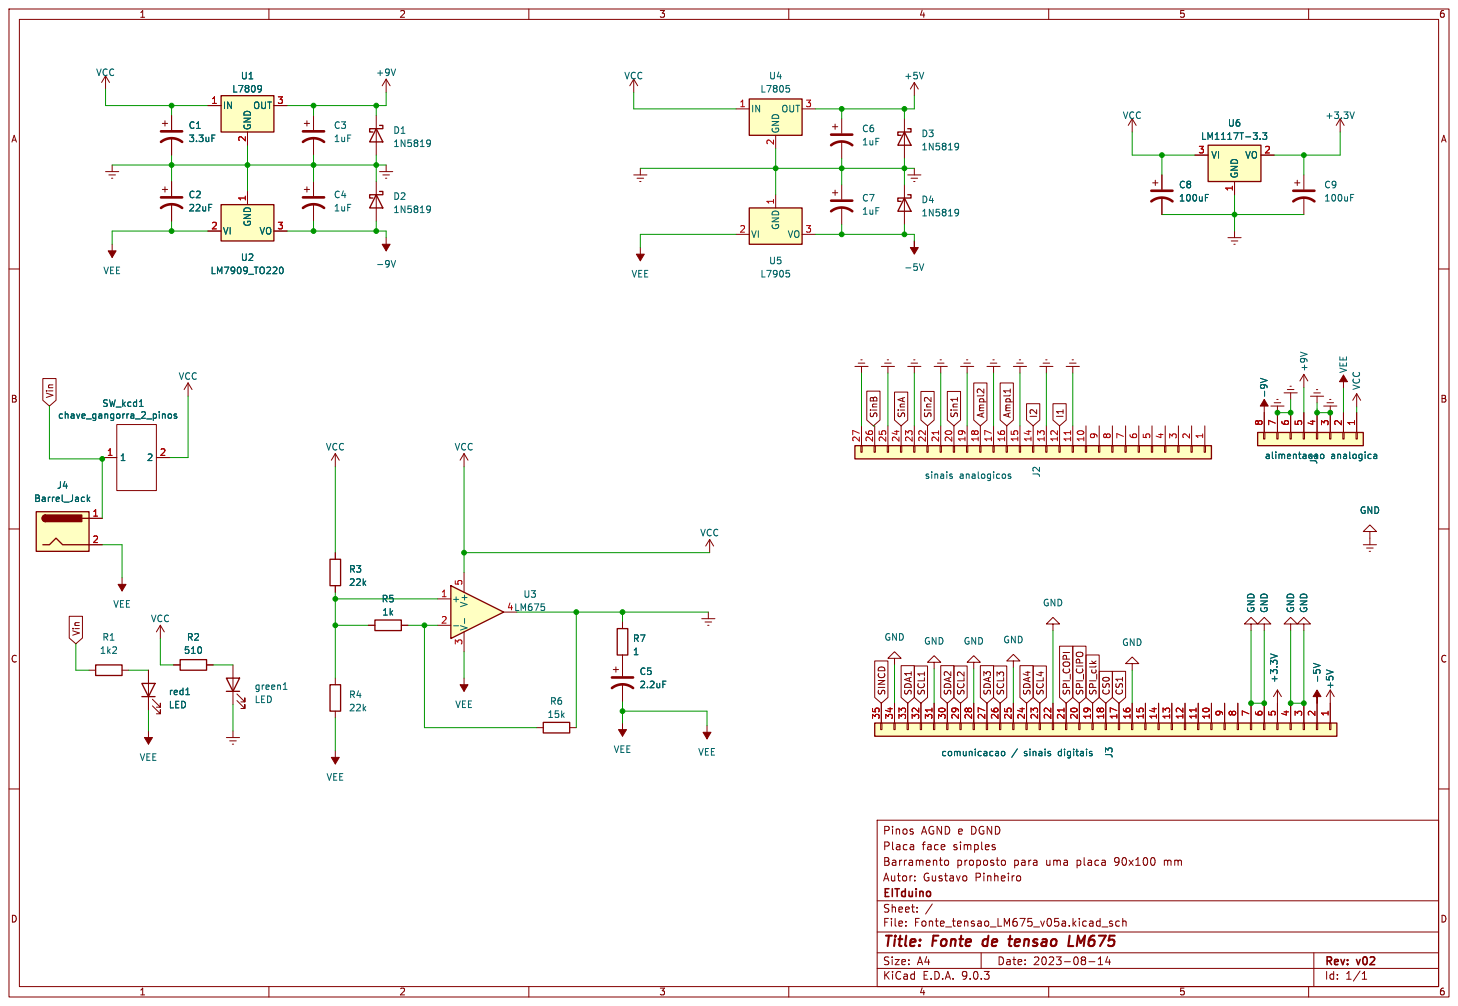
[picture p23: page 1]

1 J1alimentacao analogicaGND +3.3V GND -5V +5V GND GND GND VCC

Id: 1/1 Title: Fonte de tensao LM675

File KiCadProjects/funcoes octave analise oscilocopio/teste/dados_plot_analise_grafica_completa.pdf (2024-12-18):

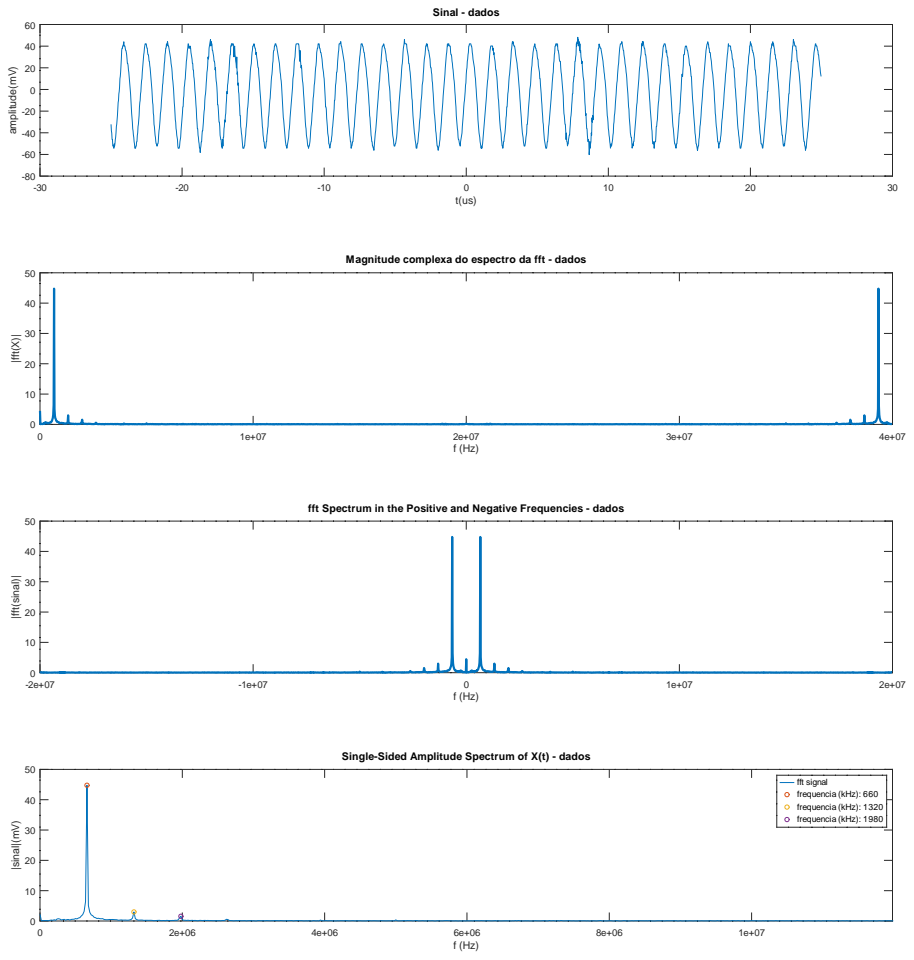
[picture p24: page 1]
Sinal - dados; amplitude(mV); |fft(X)|; |fft(sinal)|; |sinal|(mV); fft signal frequencia (kHz): 660 frequencia (kHz): 1320 frequencia (kHz): 1980

Magnitude complexa do espectro da fft - dados

fft Spectrum in the Positive and Negative Frequencies - dados

Single-Sided Amplitude Spectrum of X(t) - dados

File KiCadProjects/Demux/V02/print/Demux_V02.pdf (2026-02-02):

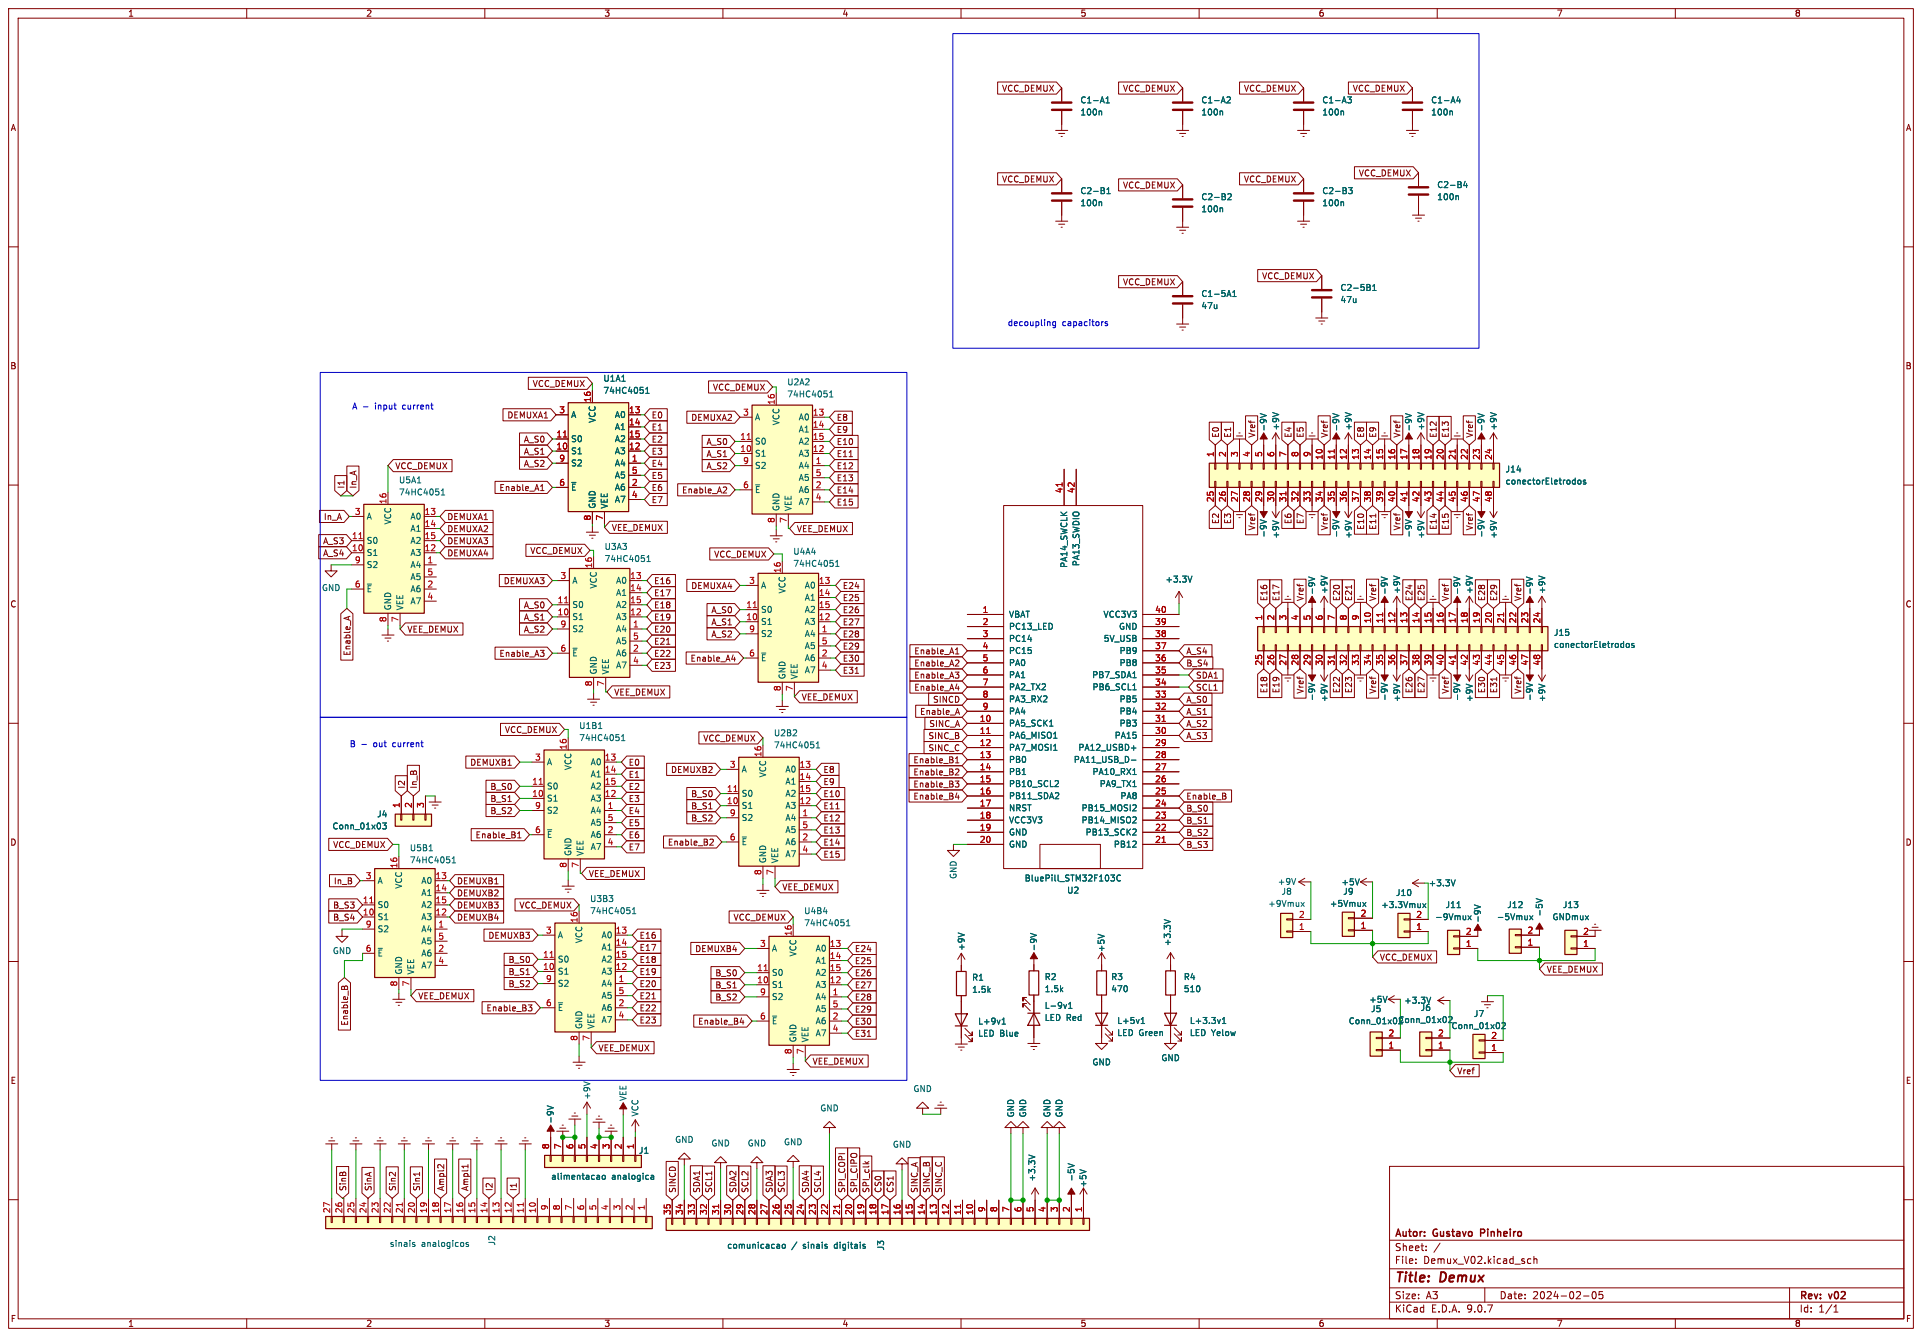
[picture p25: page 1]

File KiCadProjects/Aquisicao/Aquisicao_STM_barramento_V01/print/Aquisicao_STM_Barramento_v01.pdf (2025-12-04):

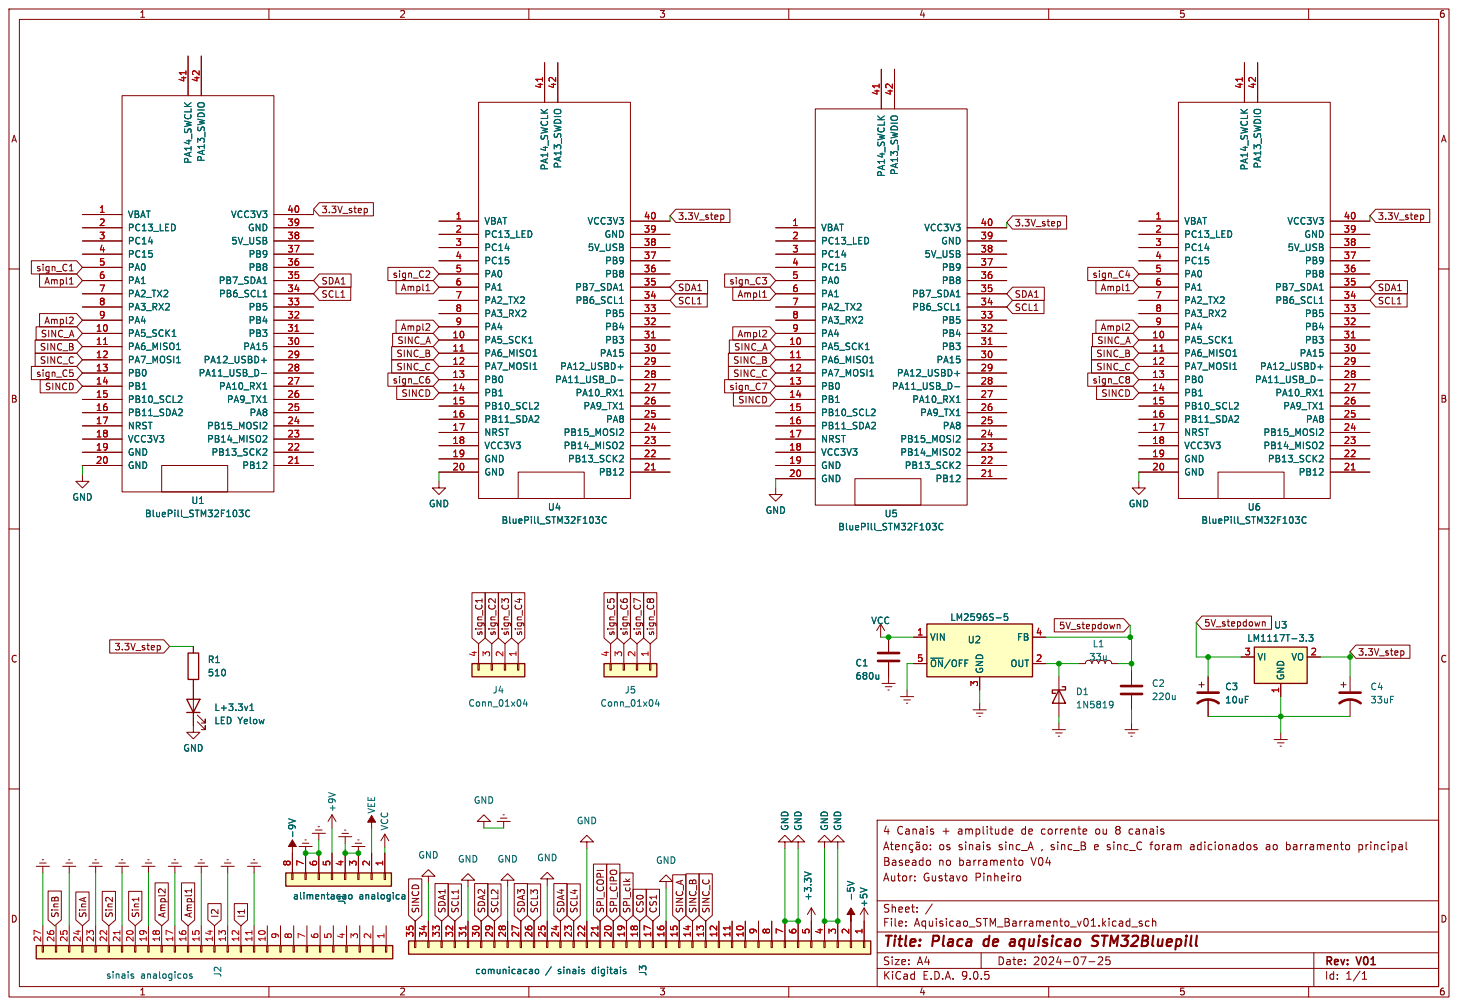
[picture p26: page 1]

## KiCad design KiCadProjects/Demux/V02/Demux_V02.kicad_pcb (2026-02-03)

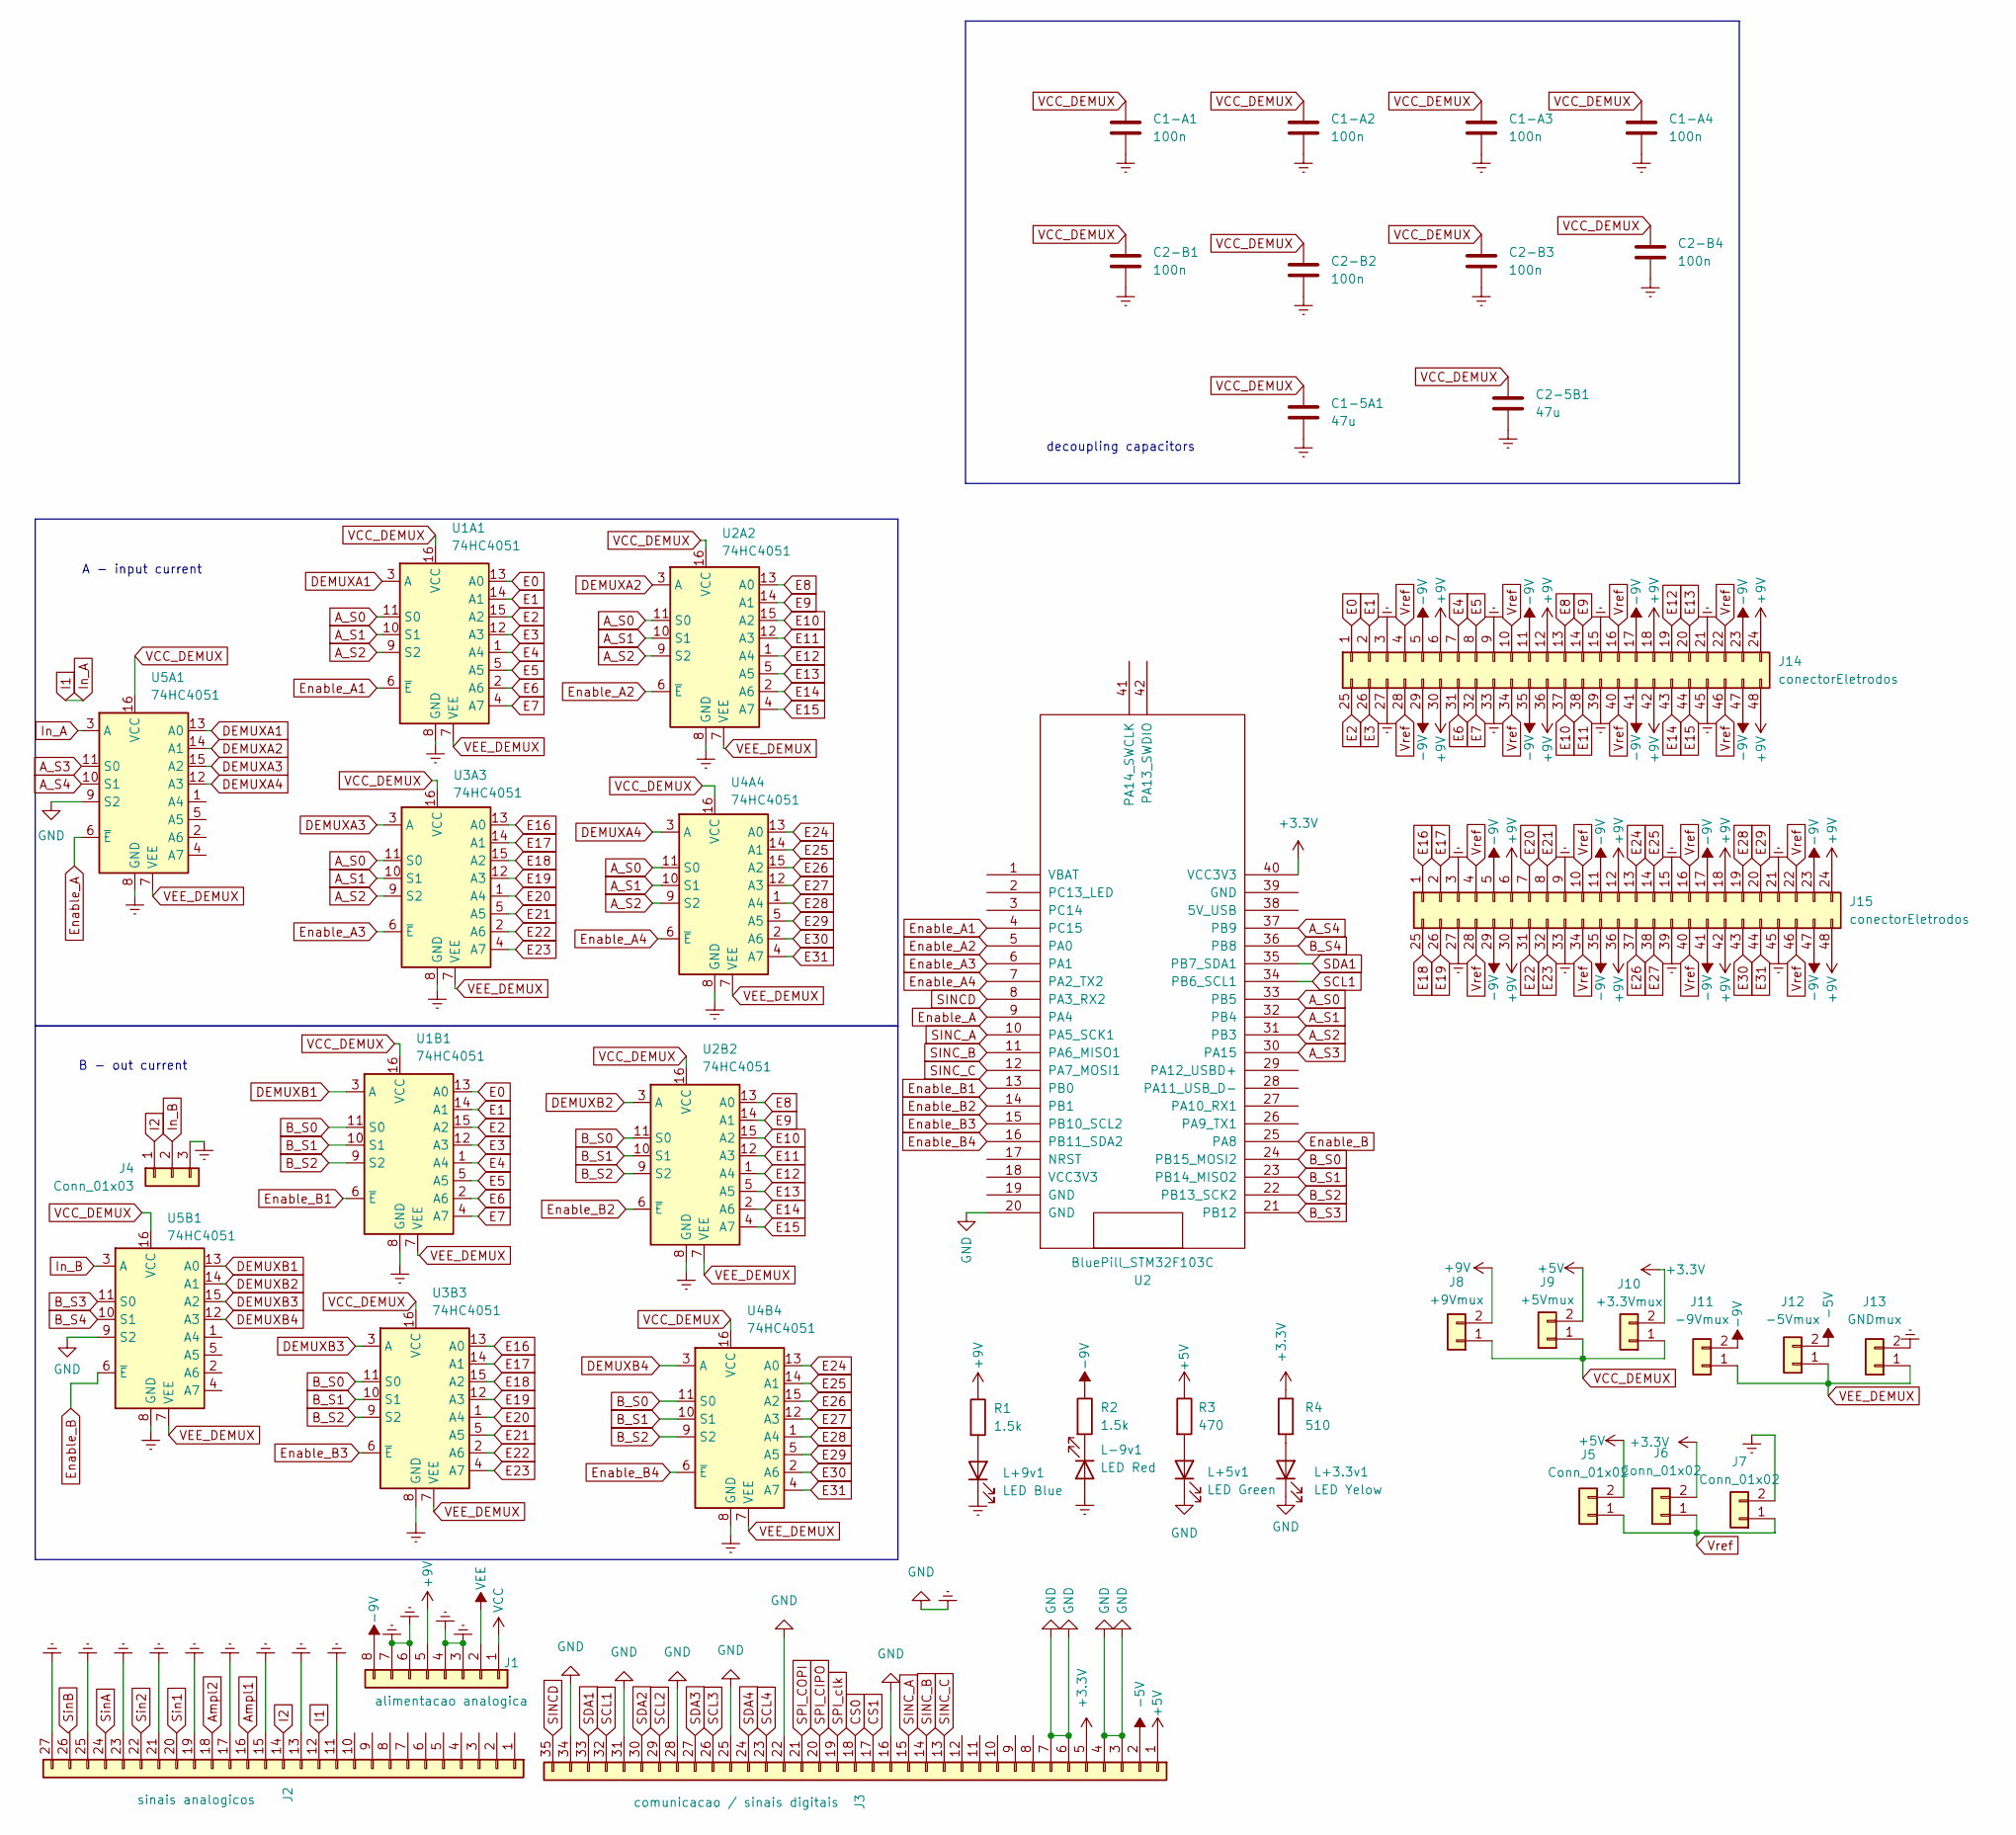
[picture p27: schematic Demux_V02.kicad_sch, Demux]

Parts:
C1-5A1, C2-5B1: 47u; CP_Radial_D5.0mm_P2.50mm
C1-A1, C1-A2, C1-A3, C1-A4, C2-B1, C2-B2, C2-B3, C2-B4: 100n; C_Disc_D3.0mm_W1.6mm_P2.50mm
J1: alimentacao analogica; PinHeader_1x08_P2.54mm_Vertical
J2: sinais analogicos; PinHeader_1x27_P2.54mm_Vertical
J3: comunicacao / sinais digitais; PinHeader_1x35_P2.54mm_Vertical
J4: Conn_01x03; PinHeader_1x03_P2.54mm_Vertical
J5, J6, J7: Conn_01x02; PinHeader_1x02_P2.54mm_Vertical
J8: +9Vmux; PinHeader_1x02_P2.54mm_Vertical
J9: +5Vmux; PinHeader_1x02_P2.54mm_Vertical
J10: +3.3Vmux; PinHeader_1x02_P2.54mm_Vertical
J11: -9Vmux; PinHeader_1x02_P2.54mm_Vertical
J12: -5Vmux; PinHeader_1x02_P2.54mm_Vertical
J13: GNDmux; PinHeader_1x02_P2.54mm_Vertical
J14, J15: conectorEletrodos; PinHeader_2x24_P2.54mm_Vertical
L+3.3v1: LED Yelow; LED_D5.0mm
L+5v1: LED Green; LED_D5.0mm
L+9v1: LED Blue; LED_D5.0mm
L-9v1: LED Red; LED_D5.0mm
R1, R2: 1.5k; R_Axial_DIN0207_L6.3mm_D2.5mm_P7.62mm_Horizontal
R3: 470; R_Axial_DIN0207_L6.3mm_D2.5mm_P7.62mm_Horizontal
R4: 510; R_Axial_DIN0207_L6.3mm_D2.5mm_P7.62mm_Horizontal
U1A1, U1B1, U2A2, U2B2, U3A3, U3B3, U4A4, U4B4, U5A1, U5B1: 74HC4051; N16
U2: BluePill_STM32F103C

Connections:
+3.3V: J3.5, J6.2, J10.2, R4.1, U2.40 (VCC3V3)
+5V: J3.1, J5.2, J9.2, R3.1
+9V: J1.5, J8.2, J14.6, J14.12, J14.18, J14.24, J14.30, J14.36, J14.42, J14.48, J15.6, J15.12, J15.18, J15.24, J15.30, J15.36, J15.42, J15.48, R1.1
-5V: J3.2, J12.2
-9V: J1.8, J11.2, J14.5, J14.11, J14.17, J14.23, J14.29, J14.35, J14.41, J14.47, J15.5, J15.11, J15.17, J15.23, J15.29, J15.35, J15.41, J15.47, R2.1
A_S0: U1A1.11 (S0), U2.33 (PB5), U2A2.11 (S0), U3A3.11 (S0), U4A4.11 (S0)
A_S1: U1A1.10 (S1), U2.32 (PB4), U2A2.10 (S1), U3A3.10 (S1), U4A4.10 (S1)
A_S2: U1A1.9 (S2), U2.31 (PB3), U2A2.9 (S2), U3A3.9 (S2), U4A4.9 (S2)
A_S3: U2.30 (PA15), U5A1.11 (S0)
A_S4: U2.37 (PB9), U5A1.10 (S1)
Ampl1: J2.16
Ampl2: J2.18
B_S0: U1B1.11 (S0), U2.24 (PB15_MOSI2), U2B2.11 (S0), U3B3.11 (S0), U4B4.11 (S0)
B_S1: U1B1.10 (S1), U2.23 (PB14_MISO2), U2B2.10 (S1), U3B3.10 (S1), U4B4.10 (S1)
B_S2: U1B1.9 (S2), U2.22 (PB13_SCK2), U2B2.9 (S2), U3B3.9 (S2), U4B4.9 (S2)
B_S3: U2.21 (PB12), U5B1.11 (S0)
B_S4: U2.36 (PB8), U5B1.10 (S1)
CS0: J3.18
CS1: J3.17
DEMUXA1: U1A1.3 (A), U5A1.13 (A0)
DEMUXA2: U2A2.3 (A), U5A1.14 (A1)
DEMUXA3: U3A3.3 (A), U5A1.15 (A2)
DEMUXA4: U4A4.3 (A), U5A1.12 (A3)
DEMUXB1: U1B1.3 (A), U5B1.13 (A0)
DEMUXB2: U2B2.3 (A), U5B1.14 (A1)
DEMUXB3: U3B3.3 (A), U5B1.15 (A2)
DEMUXB4: U4B4.3 (A), U5B1.12 (A3)
E0: J14.1, U1A1.13 (A0), U1B1.13 (A0)
E1: J14.2, U1A1.14 (A1), U1B1.14 (A1)
E2: J14.25, U1A1.15 (A2), U1B1.15 (A2)
E3: J14.26, U1A1.12 (A3), U1B1.12 (A3)
E4: J14.7, U1A1.1 (A4), U1B1.1 (A4)
E5: J14.8, U1A1.5 (A5), U1B1.5 (A5)
E6: J14.31, U1A1.2 (A6), U1B1.2 (A6)
E7: J14.32, U1A1.4 (A7), U1B1.4 (A7)
E8: J14.13, U2A2.13 (A0), U2B2.13 (A0)
E9: J14.14, U2A2.14 (A1), U2B2.14 (A1)
E10: J14.37, U2A2.15 (A2), U2B2.15 (A2)
E11: J14.38, U2A2.12 (A3), U2B2.12 (A3)
E12: J14.19, U2A2.1 (A4), U2B2.1 (A4)
E13: J14.20, U2A2.5 (A5), U2B2.5 (A5)
E14: J14.43, U2A2.2 (A6), U2B2.2 (A6)
E15: J14.44, U2A2.4 (A7), U2B2.4 (A7)
E16: J15.1, U3A3.13 (A0), U3B3.13 (A0)
E17: J15.2, U3A3.14 (A1), U3B3.14 (A1)
E18: J15.25, U3A3.15 (A2), U3B3.15 (A2)
E19: J15.26, U3A3.12 (A3), U3B3.12 (A3)
E20: J15.7, U3A3.1 (A4), U3B3.1 (A4)
E21: J15.8, U3A3.5 (A5), U3B3.5 (A5)
E22: J15.31, U3A3.2 (A6), U3B3.2 (A6)
E23: J15.32, U3A3.4 (A7), U3B3.4 (A7)
E24: J15.13, U4A4.13 (A0), U4B4.13 (A0)
E25: J15.14, U4A4.14 (A1), U4B4.14 (A1)
E26: J15.37, U4A4.15 (A2), U4B4.15 (A2)
E27: J15.38, U4A4.12 (A3), U4B4.12 (A3)
E28: J15.19, U4A4.1 (A4), U4B4.1 (A4)
E29: J15.20, U4A4.5 (A5), U4B4.5 (A5)
E30: J15.43, U4A4.2 (A6), U4B4.2 (A6)
E31: J15.44, U4A4.4 (A7), U4B4.4 (A7)
Earth: C1-5A1.2, C1-A1.2, C1-A2.2, C1-A3.2, C1-A4.2, C2-5B1.2, C2-B1.2, C2-B2.2, C2-B3.2, C2-B4.2, J1.3, J1.4, J1.6, J1.7, J2.11, J2.13, J2.15, J2.17, J2.19, J2.21, J2.23, J2.25, J2.27, J3.3, J3.4, J3.6, J3.7, J3.16, J3.22, J3.25, J3.28, J3.31, J3.34, J4.3, J7.2, J13.2, J14.3, J14.9, J14.15, J14.21, J14.27, J14.33, J14.39, J14.45, J15.3, J15.9, J15.15, J15.21, J15.27, J15.33, J15.39, J15.45, L+3.3v1.1 (K), L+5v1.1 (K), L+9v1.1 (K), L-9v1.2 (A), U1A1.8 (GND), U1B1.8 (GND), U2.20 (GND), U2A2.8 (GND), U2B2.8 (GND), U3A3.8 (GND), U3B3.8 (GND), U4A4.8 (GND), U4B4.8 (GND), U5A1.8 (GND), U5A1.9 (S2), U5B1.8 (GND), U5B1.9 (S2)
Enable_A: U2.9 (PA4), U5A1.6 (~E)
Enable_A1: U1A1.6 (~E), U2.4 (PC15)
Enable_A2: U2.5 (PA0), U2A2.6 (~E)
Enable_A3: U2.6 (PA1), U3A3.6 (~E)
Enable_A4: U2.7 (PA2_TX2), U4A4.6 (~E)
Enable_B: U2.25 (PA8), U5B1.6 (~E)
Enable_B1: U1B1.6 (~E), U2.13 (PB0)
Enable_B2: U2.14 (PB1), U2B2.6 (~E)
Enable_B3: U2.15 (PB10_SCL2), U3B3.6 (~E)
Enable_B4: U2.16 (PB11_SDA2), U4B4.6 (~E)
I1: J2.12, U5A1.3 (A)
I2: J2.14, J4.1
In_B: J4.2, U5B1.3 (A)
unnamed: L+3.3v1.2 (A), R4.2
unnamed: L+5v1.2 (A), R3.2
unnamed: L+9v1.2 (A), R1.2
unnamed: L-9v1.1 (K), R2.2
SCL1: J3.32, U2.34 (PB6_SCL1)
SCL2: J3.29
SCL3: J3.26
SCL4: J3.23
SDA1: J3.33, U2.35 (PB7_SDA1)
SDA2: J3.30
SDA3: J3.27
SDA4: J3.24
SINCD: J3.35, U2.8 (PA3_RX2)
SINC_A: J3.15, U2.10 (PA5_SCK1)
SINC_B: J3.14, U2.11 (PA6_MISO1)
SINC_C: J3.13, U2.12 (PA7_MOSI1)
SPI_CIPO: J3.20
SPI_COPI: J3.21
SPI_clk: J3.19
Sin1: J2.20
Sin2: J2.22
SinA: J2.24
SinB: J2.26
VCC: J1.1
VCC_DEMUX: C1-5A1.1, C1-A1.1, C1-A2.1, C1-A3.1, C1-A4.1, C2-5B1.1, C2-B1.1, C2-B2.1, C2-B3.1, C2-B4.1, J8.1, J9.1, J10.1, U1A1.16 (VCC), U1B1.16 (VCC), U2A2.16 (VCC), U2B2.16 (VCC), U3A3.16 (VCC), U3B3.16 (VCC), U4A4.16 (VCC), U4B4.16 (VCC), U5A1.16 (VCC), U5B1.16 (VCC)
VEE: J1.2
VEE_DEMUX: J11.1, J12.1, J13.1, U1A1.7 (VEE), U1B1.7 (VEE), U2A2.7 (VEE), U2B2.7 (VEE), U3A3.7 (VEE), U3B3.7 (VEE), U4A4.7 (VEE), U4B4.7 (VEE), U5A1.7 (VEE), U5B1.7 (VEE)
Vref: J5.1, J6.1, J7.1, J14.4, J14.10, J14.16, J14.22, J14.28, J14.34, J14.40, J14.46, J15.4, J15.10, J15.16, J15.22, J15.28, J15.34, J15.40, J15.46

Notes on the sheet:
decoupling capacitors
A - input current
B - out current

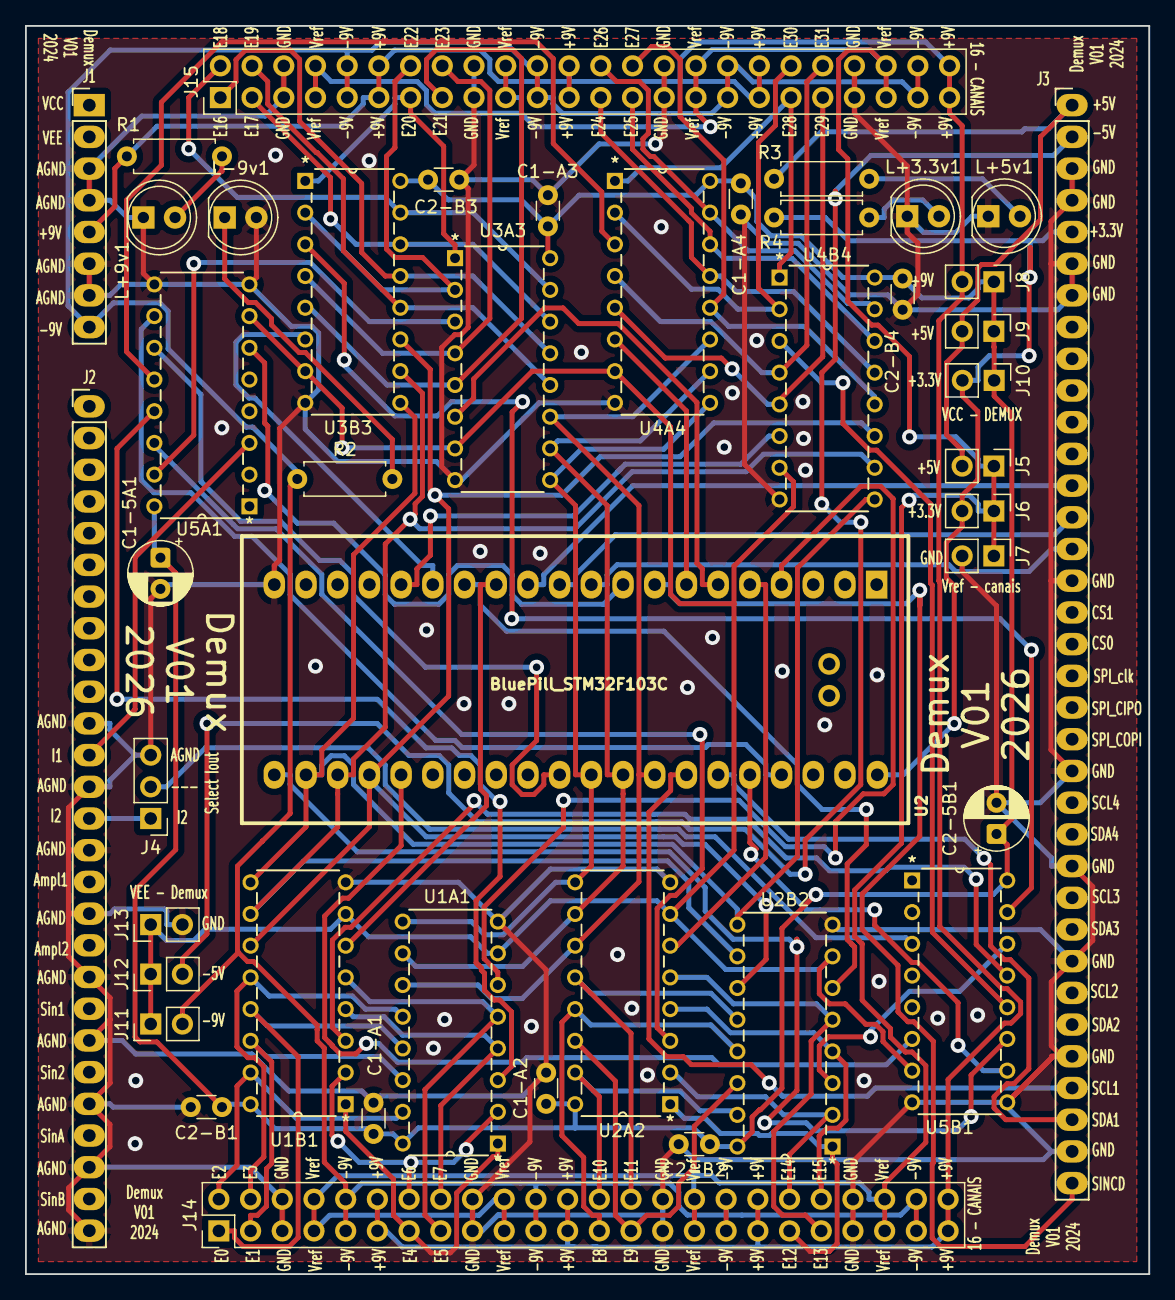
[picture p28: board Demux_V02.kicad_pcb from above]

Board: 2 copper layers, 90.0 x 100.0 mm, 44 parts (0 on the bottom side), 82 nets.

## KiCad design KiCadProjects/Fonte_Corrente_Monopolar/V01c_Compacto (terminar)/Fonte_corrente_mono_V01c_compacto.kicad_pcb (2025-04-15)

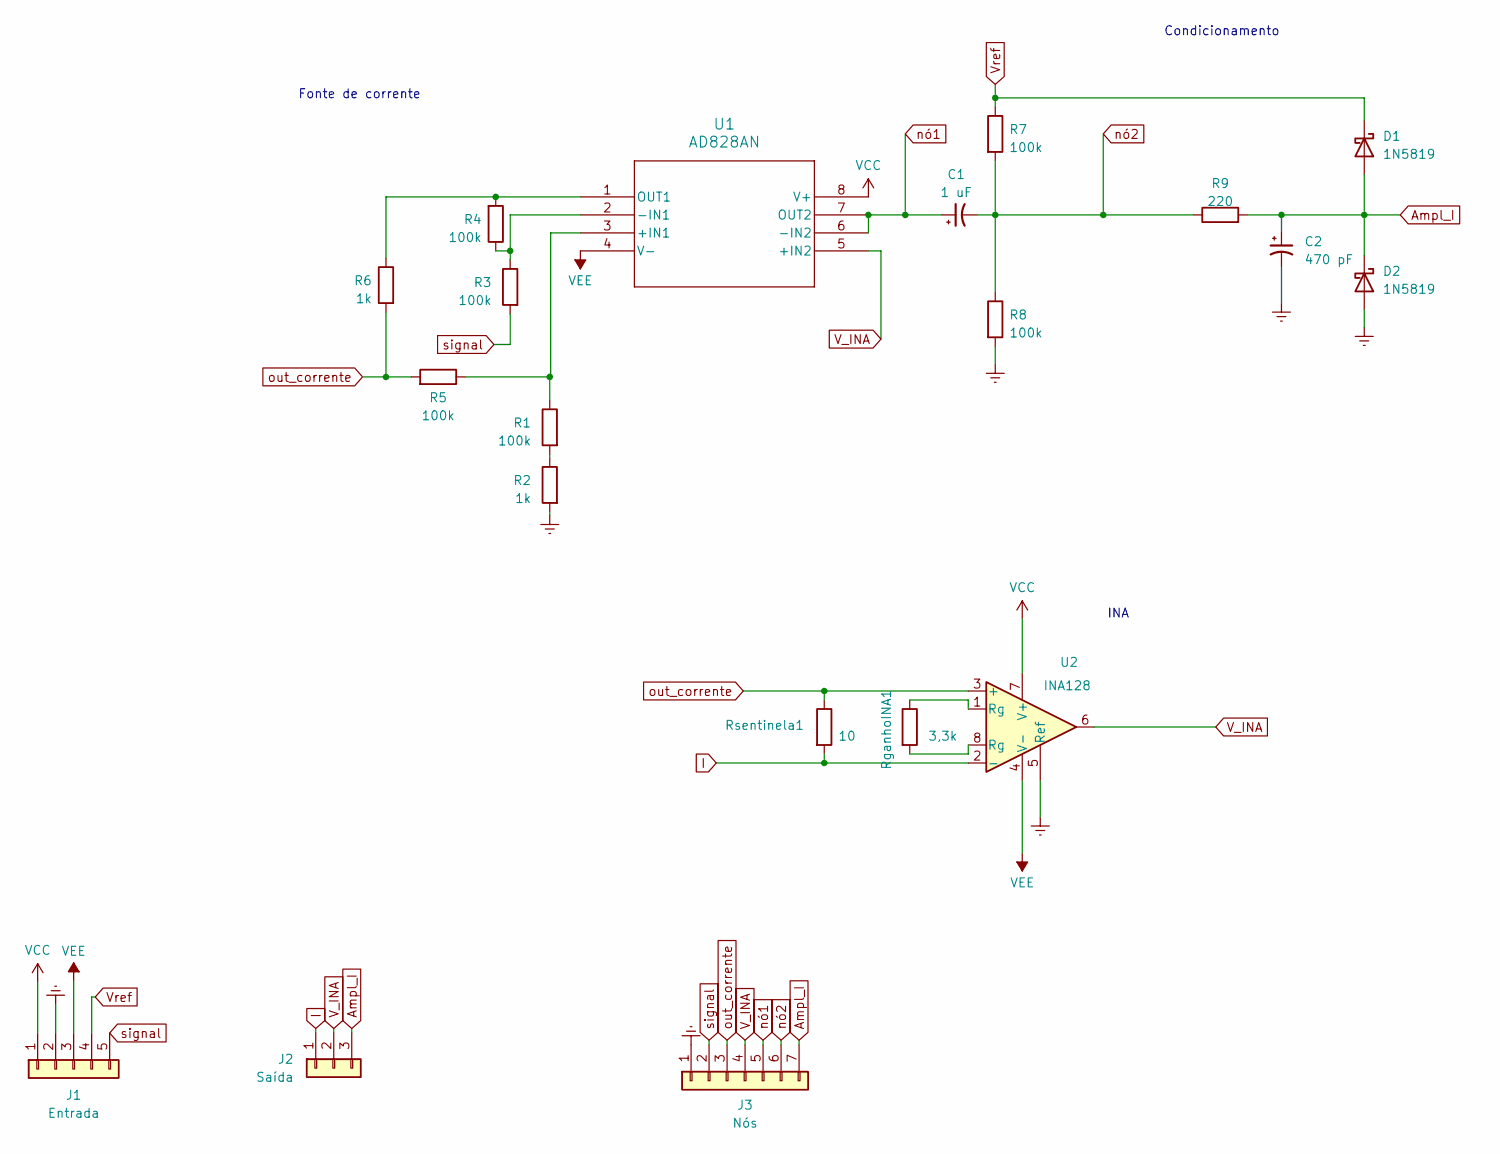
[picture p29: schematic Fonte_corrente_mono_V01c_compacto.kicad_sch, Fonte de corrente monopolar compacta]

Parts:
C1: 1 uF; CP_Radial_D5.0mm_P2.50mm
C2: 470 pF; CP_Radial_D5.0mm_P2.50mm
D1, D2: 1N5819; D_DO-41_SOD81_P10.16mm_Horizontal
J1: Entrada; PinSocket_1x05_P2.54mm_Vertical
J2: Saída; PinSocket_1x03_P2.54mm_Vertical
J3: Nós; PinHeader_1x07_P2.54mm_Vertical
R1, R3, R4, R5, R7, R8: 100k; R_Axial_DIN0207_L6.3mm_D2.5mm_P7.62mm_Horizontal
R2, R6: 1k; R_Axial_DIN0207_L6.3mm_D2.5mm_P7.62mm_Horizontal
R9: 220; R_Axial_DIN0207_L6.3mm_D2.5mm_P7.62mm_Horizontal
RganhoINA1: 3,3k; R_Axial_DIN0207_L6.3mm_D2.5mm_P7.62mm_Horizontal
Rsentinela1: 10; R_Axial_DIN0207_L6.3mm_D2.5mm_P7.62mm_Horizontal
U1: AD828AN; N_8_ADI
U2: INA128; DIP-8_W7.62mm

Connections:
Ampl_I: C2.1, D1.2 (A), D2.1 (K), J2.3, J3.7, R9.2
Earth: C2.2, D2.2 (A), J1.2, J3.1, R2.2, R8.2, U2.5 (Ref)
I: J2.1, Rsentinela1.2, U2.2 (-)
unnamed: R1.2, R2.1
unnamed: RganhoINA1.1, U2.1 (Rg)
unnamed: RganhoINA1.2, U2.8 (Rg)
unnamed: R1.1, R5.1, U1.3 (+IN1)
unnamed: R3.1, R4.1, U1.2 (-IN1)
unnamed: R4.2, R6.1, U1.1 (OUT1)
VCC: J1.1, U1.8 (V+), U2.7 (V+)
VEE: J1.3, U1.4 (V-), U2.4 (V-)
V_INA: J2.2, J3.4, U1.5 (+IN2), U2.6
Vref: D1.1 (K), J1.4, R7.1
nó1: C1.1, J3.5, U1.6 (-IN2), U1.7 (OUT2)
nó2: C1.2, J3.6, R7.2, R8.1, R9.1
out_corrente: J3.3, R5.2, R6.2, Rsentinela1.1, U2.3 (+)
signal: J1.5, J3.2, R3.2

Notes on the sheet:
Condicionamento
Fonte de corrente
INA

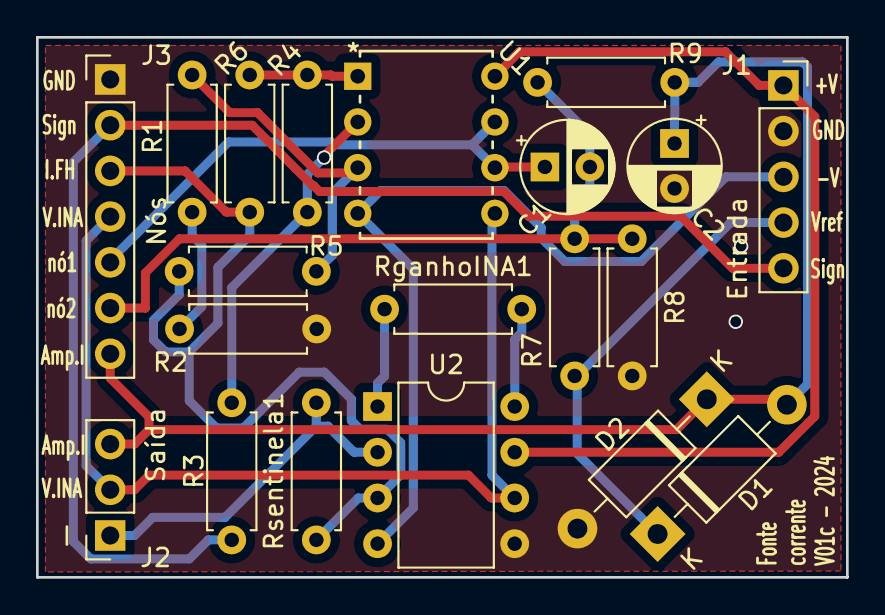
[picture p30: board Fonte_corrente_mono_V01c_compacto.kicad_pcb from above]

Board: 2 copper layers, 45.0 x 30.0 mm, 20 parts (0 on the bottom side), 17 nets.

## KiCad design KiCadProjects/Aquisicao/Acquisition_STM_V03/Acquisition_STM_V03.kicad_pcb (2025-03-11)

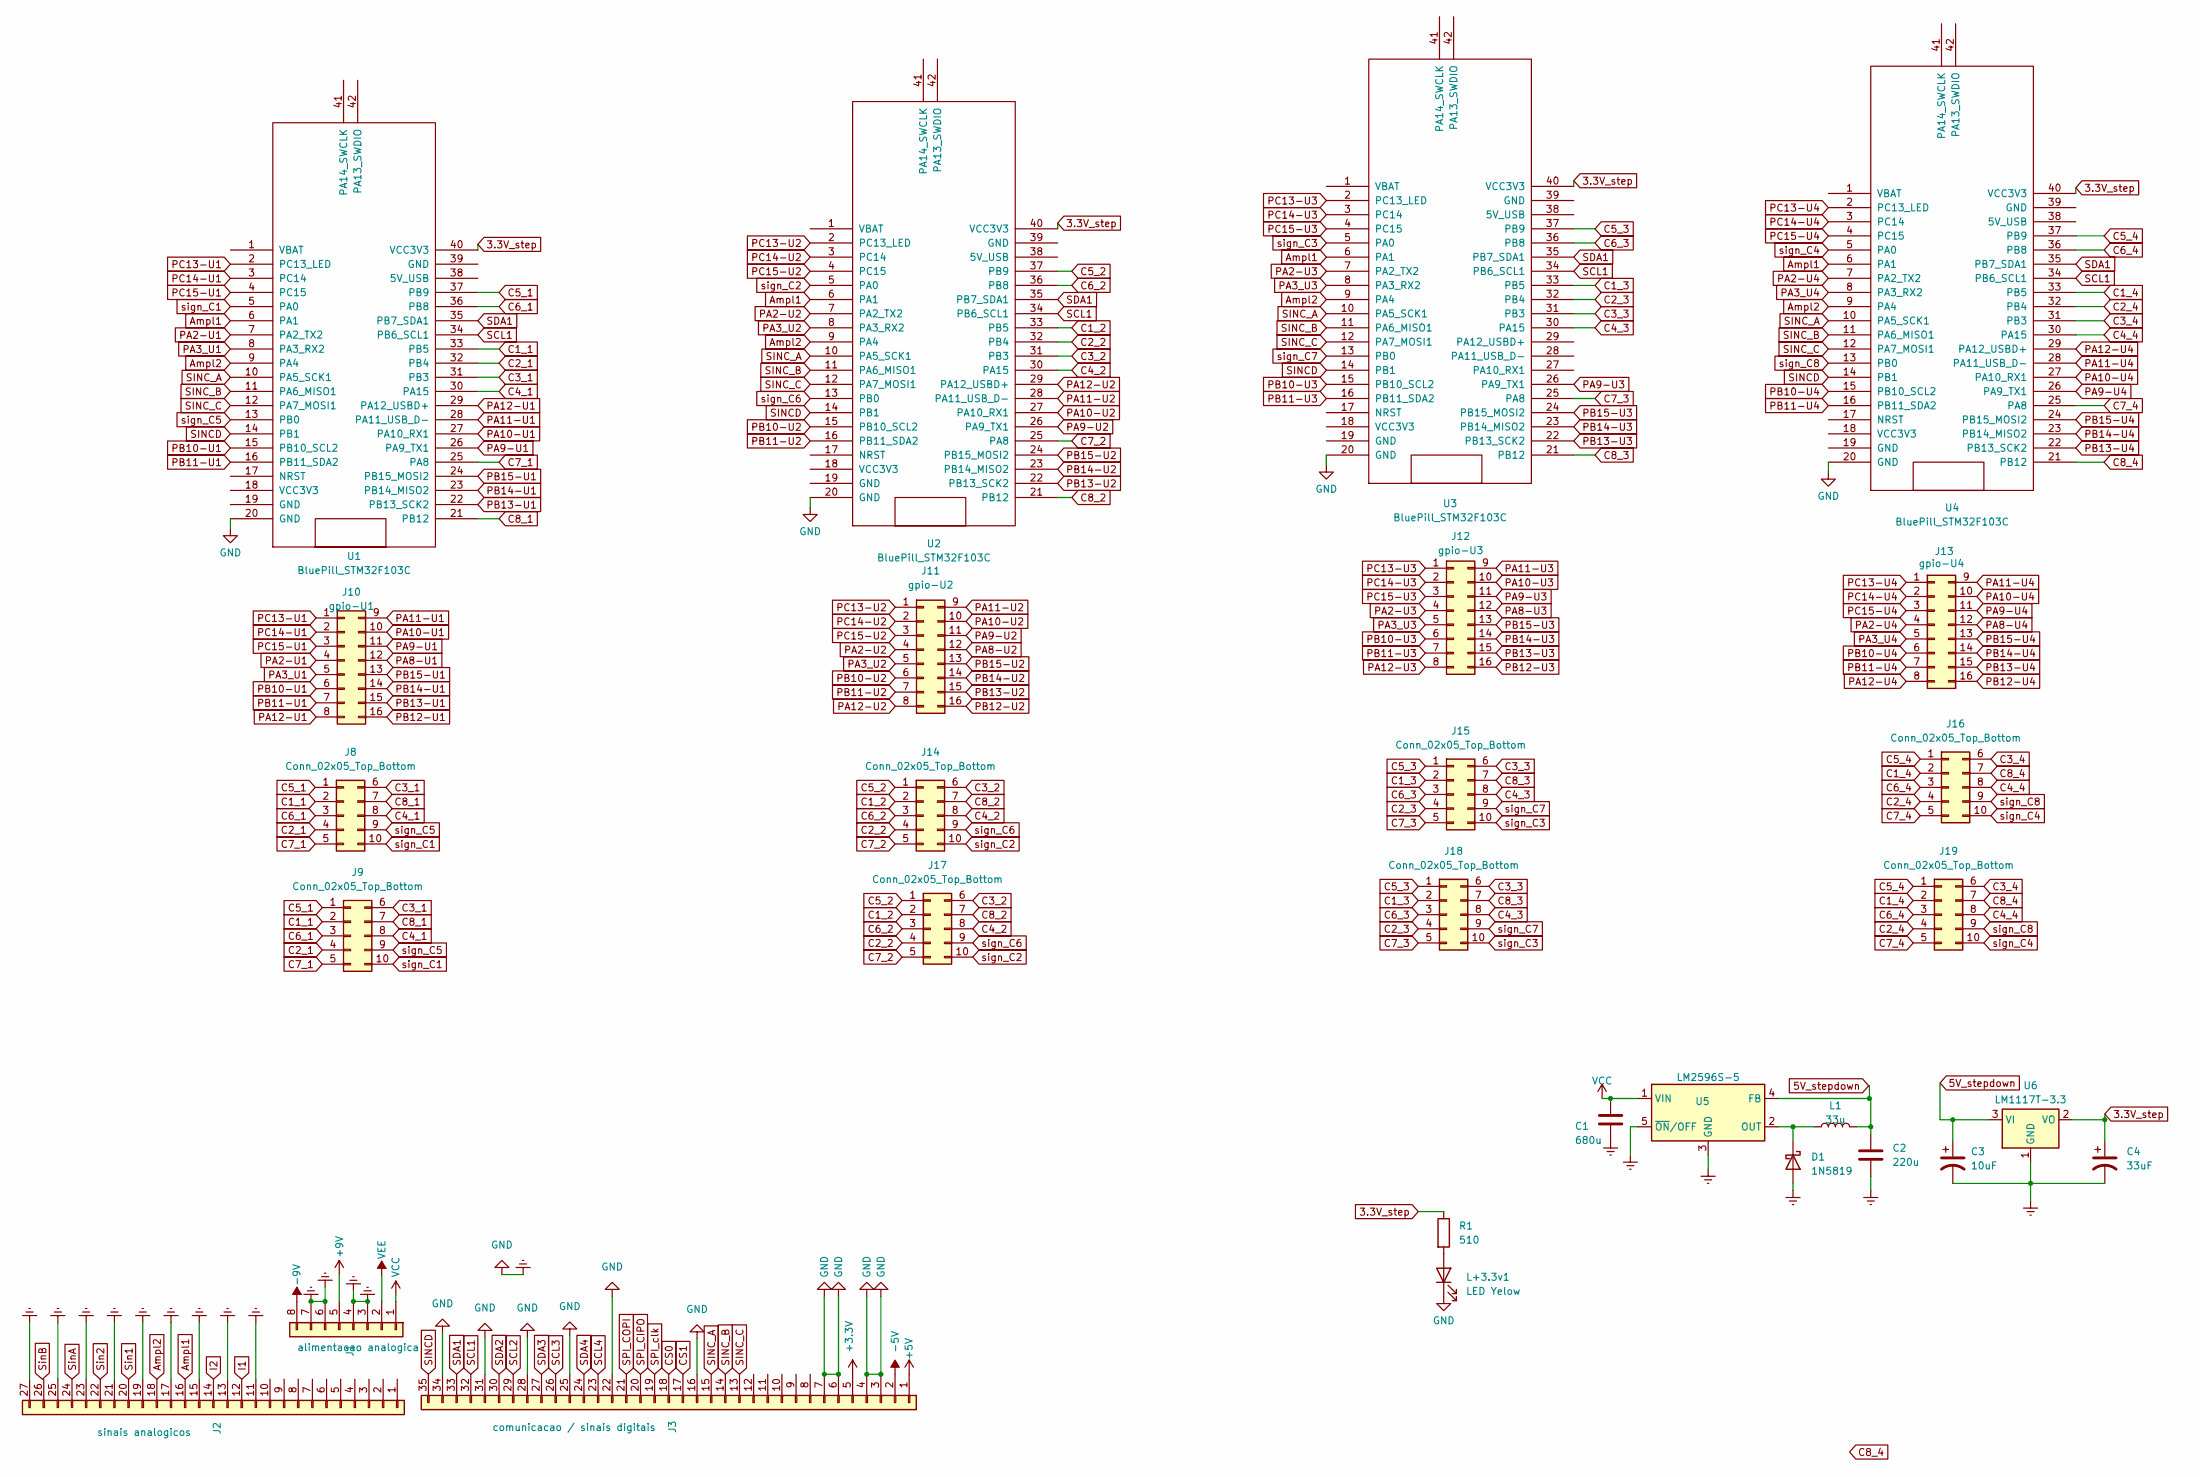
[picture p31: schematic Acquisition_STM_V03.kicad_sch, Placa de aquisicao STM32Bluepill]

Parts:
C1: 680u; CP_Radial_D5.0mm_P2.50mm
C2: 220u; CP_Radial_D5.0mm_P2.50mm
C3: 10uF; CP_Radial_Tantal_D4.5mm_P2.50mm
C4: 33uF; CP_Radial_Tantal_D4.5mm_P2.50mm
D1: 1N5819; D_DO-41_SOD81_P10.16mm_Horizontal
J1: alimentacao analogica; PinHeader_1x08_P2.54mm_Vertical
J2: sinais analogicos; PinHeader_1x27_P2.54mm_Vertical
J3: comunicacao / sinais digitais; PinHeader_1x35_P2.54mm_Vertical
J8, J9, J14, J15, J16, J17, J18, J19: Conn_02x05_Top_Bottom; PinHeader_2x05_P2.54mm_Horizontal
J10: gpio-U1; PinHeader_2x08_P2.54mm_Vertical
J11: gpio-U2; PinHeader_2x08_P2.54mm_Vertical
J12: gpio-U3; PinHeader_2x08_P2.54mm_Vertical
J13: gpio-U4; PinHeader_2x08_P2.54mm_Vertical
L1: 33u; L_7.3x7.3_H4.5
L+3.3v1: LED Yelow; LED_D5.0mm
R1: 510; R_Axial_DIN0207_L6.3mm_D2.5mm_P7.62mm_Horizontal
U1, U2, U3, U4: BluePill_STM32F103C
U5: LM2596S-5; TO-220-5_P3.4x3.7mm_StaggerOdd_Lead3.8mm_Vertical
U6: LM1117T-3.3; TO-220-3_Vertical

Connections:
3.3V_step: C4.1, R1.1, U1.40 (VCC3V3), U2.40 (VCC3V3), U3.40 (VCC3V3), U4.40 (VCC3V3), U6.2 (VO)
5V_stepdown: C2.1, C3.1, L1.2, U5.4 (FB), U6.3 (VI)
+3.3V: J3.5
+5V: J3.1
+9V: J1.5
-5V: J3.2
-9V: J1.8
Ampl1: J2.16, U1.6 (PA1), U2.6 (PA1), U3.6 (PA1), U4.6 (PA1)
Ampl2: J2.18, U1.9 (PA4), U2.9 (PA4), U3.9 (PA4), U4.9 (PA4)
C1_1: J8.2, J9.2, U1.33 (PB5)
C1_2: J14.2, J17.2, U2.33 (PB5)
C1_3: J15.2, J18.2, U3.33 (PB5)
C1_4: J16.2, J19.2, U4.33 (PB5)
C2_1: J8.4, J9.4, U1.32 (PB4)
C2_2: J14.4, J17.4, U2.32 (PB4)
C2_3: J15.4, J18.4, U3.32 (PB4)
C2_4: J16.4, J19.4, U4.32 (PB4)
C3_1: J8.6, J9.6, U1.31 (PB3)
C3_2: J14.6, J17.6, U2.31 (PB3)
C3_3: J15.6, J18.6, U3.31 (PB3)
C3_4: J16.6, J19.6, U4.31 (PB3)
C4_1: J8.8, J9.8, U1.30 (PA15)
C4_2: J14.8, J17.8, U2.30 (PA15)
C4_3: J15.8, J18.8, U3.30 (PA15)
C4_4: J16.8, J19.8, U4.30 (PA15)
C5_1: J8.1, J9.1, U1.37 (PB9)
C5_2: J14.1, J17.1, U2.37 (PB9)
C5_3: J15.1, J18.1, U3.37 (PB9)
C5_4: J16.1, J19.1, U4.37 (PB9)
C6_1: J8.3, J9.3, U1.36 (PB8)
C6_2: J14.3, J17.3, U2.36 (PB8)
C6_3: J15.3, J18.3, U3.36 (PB8)
C6_4: J16.3, J19.3, U4.36 (PB8)
C7_1: J8.5, J9.5, U1.25 (PA8)
C7_2: J14.5, J17.5, U2.25 (PA8)
C7_3: J15.5, J18.5, U3.25 (PA8)
C7_4: J16.5, J19.5, U4.25 (PA8)
C8_1: J8.7, J9.7, U1.21 (PB12)
C8_2: J14.7, J17.7, U2.21 (PB12)
C8_3: J15.7, J18.7, U3.21 (PB12)
C8_4: J16.7, J19.7, U4.21 (PB12)
CS0: J3.18
CS1: J3.17
Earth: C1.2, C2.2, C3.2, C4.2, D1.2 (A), J1.3, J1.4, J1.6, J1.7, J2.11, J2.13, J2.15, J2.17, J2.19, J2.21, J2.23, J2.25, J2.27, J3.3, J3.4, J3.6, J3.7, J3.16, J3.22, J3.25, J3.28, J3.31, J3.34, L+3.3v1.1 (K), U1.20 (GND), U2.20 (GND), U3.20 (GND), U4.20 (GND), U5.3 (GND), U5.5 (~ON/OFF), U6.1 (GND)
I1: J2.12
I2: J2.14
unnamed: D1.1 (K), L1.1, U5.2 (OUT)
unnamed: L+3.3v1.2 (A), R1.2
PA2-U1: J10.4, U1.7 (PA2_TX2)
PA2-U2: J11.4, U2.7 (PA2_TX2)
PA2-U3: J12.4, U3.7 (PA2_TX2)
PA2-U4: J13.4, U4.7 (PA2_TX2)
PA3_U1: J10.5, U1.8 (PA3_RX2)
PA3_U2: J11.5, U2.8 (PA3_RX2)
PA3_U3: J12.5, U3.8 (PA3_RX2)
PA3_U4: J13.5, U4.8 (PA3_RX2)
PA8-U1: J10.12
PA8-U2: J11.12
PA8-U3: J12.12
PA8-U4: J13.12
PA9-U1: J10.11, U1.26 (PA9_TX1)
PA9-U2: J11.11, U2.26 (PA9_TX1)
PA9-U3: J12.11, U3.26 (PA9_TX1)
PA9-U4: J13.11, U4.26 (PA9_TX1)
PA10-U1: J10.10, U1.27 (PA10_RX1)
PA10-U2: J11.10, U2.27 (PA10_RX1)
PA10-U3: J12.10
PA10-U4: J13.10, U4.27 (PA10_RX1)
PA11-U1: J10.9, U1.28 (PA11_USB_D-)
PA11-U2: J11.9, U2.28 (PA11_USB_D-)
PA11-U3: J12.9
PA11-U4: J13.9, U4.28 (PA11_USB_D-)
PA12-U1: J10.8, U1.29 (PA12_USBD+)
PA12-U2: J11.8, U2.29 (PA12_USBD+)
PA12-U3: J12.8
PA12-U4: J13.8, U4.29 (PA12_USBD+)
PB10-U1: J10.6, U1.15 (PB10_SCL2)
PB10-U2: J11.6, U2.15 (PB10_SCL2)
PB10-U3: J12.6, U3.15 (PB10_SCL2)
PB10-U4: J13.6, U4.15 (PB10_SCL2)
PB11-U1: J10.7, U1.16 (PB11_SDA2)
PB11-U2: J11.7, U2.16 (PB11_SDA2)
PB11-U3: J12.7, U3.16 (PB11_SDA2)
PB11-U4: J13.7, U4.16 (PB11_SDA2)
PB12-U1: J10.16
PB12-U2: J11.16
PB12-U3: J12.16
PB12-U4: J13.16
PB13-U1: J10.15, U1.22 (PB13_SCK2)
PB13-U2: J11.15, U2.22 (PB13_SCK2)
PB13-U3: J12.15, U3.22 (PB13_SCK2)
PB13-U4: J13.15, U4.22 (PB13_SCK2)
PB14-U1: J10.14, U1.23 (PB14_MISO2)
PB14-U2: J11.14, U2.23 (PB14_MISO2)
PB14-U3: J12.14, U3.23 (PB14_MISO2)
PB14-U4: J13.14, U4.23 (PB14_MISO2)
PB15-U1: J10.13, U1.24 (PB15_MOSI2)
PB15-U2: J11.13, U2.24 (PB15_MOSI2)
PB15-U3: J12.13, U3.24 (PB15_MOSI2)
PB15-U4: J13.13, U4.24 (PB15_MOSI2)
PC13-U1: J10.1, U1.2 (PC13_LED)
PC13-U2: J11.1, U2.2 (PC13_LED)
PC13-U3: J12.1, U3.2 (PC13_LED)
PC13-U4: J13.1, U4.2 (PC13_LED)
PC14-U1: J10.2, U1.3 (PC14)
PC14-U2: J11.2, U2.3 (PC14)
PC14-U3: J12.2, U3.3 (PC14)
PC14-U4: J13.2, U4.3 (PC14)
PC15-U1: J10.3, U1.4 (PC15)
PC15-U2: J11.3, U2.4 (PC15)
PC15-U3: J12.3, U3.4 (PC15)
PC15-U4: J13.3, U4.4 (PC15)
SCL1: J3.32, U1.34 (PB6_SCL1), U2.34 (PB6_SCL1), U3.34 (PB6_SCL1), U4.34 (PB6_SCL1)
SCL2: J3.29
SCL3: J3.26
SCL4: J3.23
SDA1: J3.33, U1.35 (PB7_SDA1), U2.35 (PB7_SDA1), U3.35 (PB7_SDA1), U4.35 (PB7_SDA1)
SDA2: J3.30
SDA3: J3.27
SDA4: J3.24
SINCD: J3.35, U1.14 (PB1), U2.14 (PB1), U3.14 (PB1), U4.14 (PB1)
SINC_A: J3.15, U1.10 (PA5_SCK1), U2.10 (PA5_SCK1), U3.10 (PA5_SCK1), U4.10 (PA5_SCK1)
SINC_B: J3.14, U1.11 (PA6_MISO1), U2.11 (PA6_MISO1), U3.11 (PA6_MISO1), U4.11 (PA6_MISO1)
SINC_C: J3.13, U1.12 (PA7_MOSI1), U2.12 (PA7_MOSI1), U3.12 (PA7_MOSI1), U4.12 (PA7_MOSI1)
SPI_CIPO: J3.20
SPI_COPI: J3.21
SPI_clk: J3.19
Sin1: J2.20
Sin2: J2.22
SinA: J2.24
SinB: J2.26
VCC: C1.1, J1.1, U5.1 (VIN)
VEE: J1.2
sign_C1: J8.10, J9.10, U1.5 (PA0)
sign_C2: J14.10, J17.10, U2.5 (PA0)
sign_C3: J15.10, J18.10, U3.5 (PA0)
sign_C4: J16.10, J19.10, U4.5 (PA0)
sign_C5: J8.9, J9.9, U1.13 (PB0)
sign_C6: J14.9, J17.9, U2.13 (PB0)
sign_C7: J15.9, J18.9, U3.13 (PB0)
sign_C8: J16.9, J19.9, U4.13 (PB0)

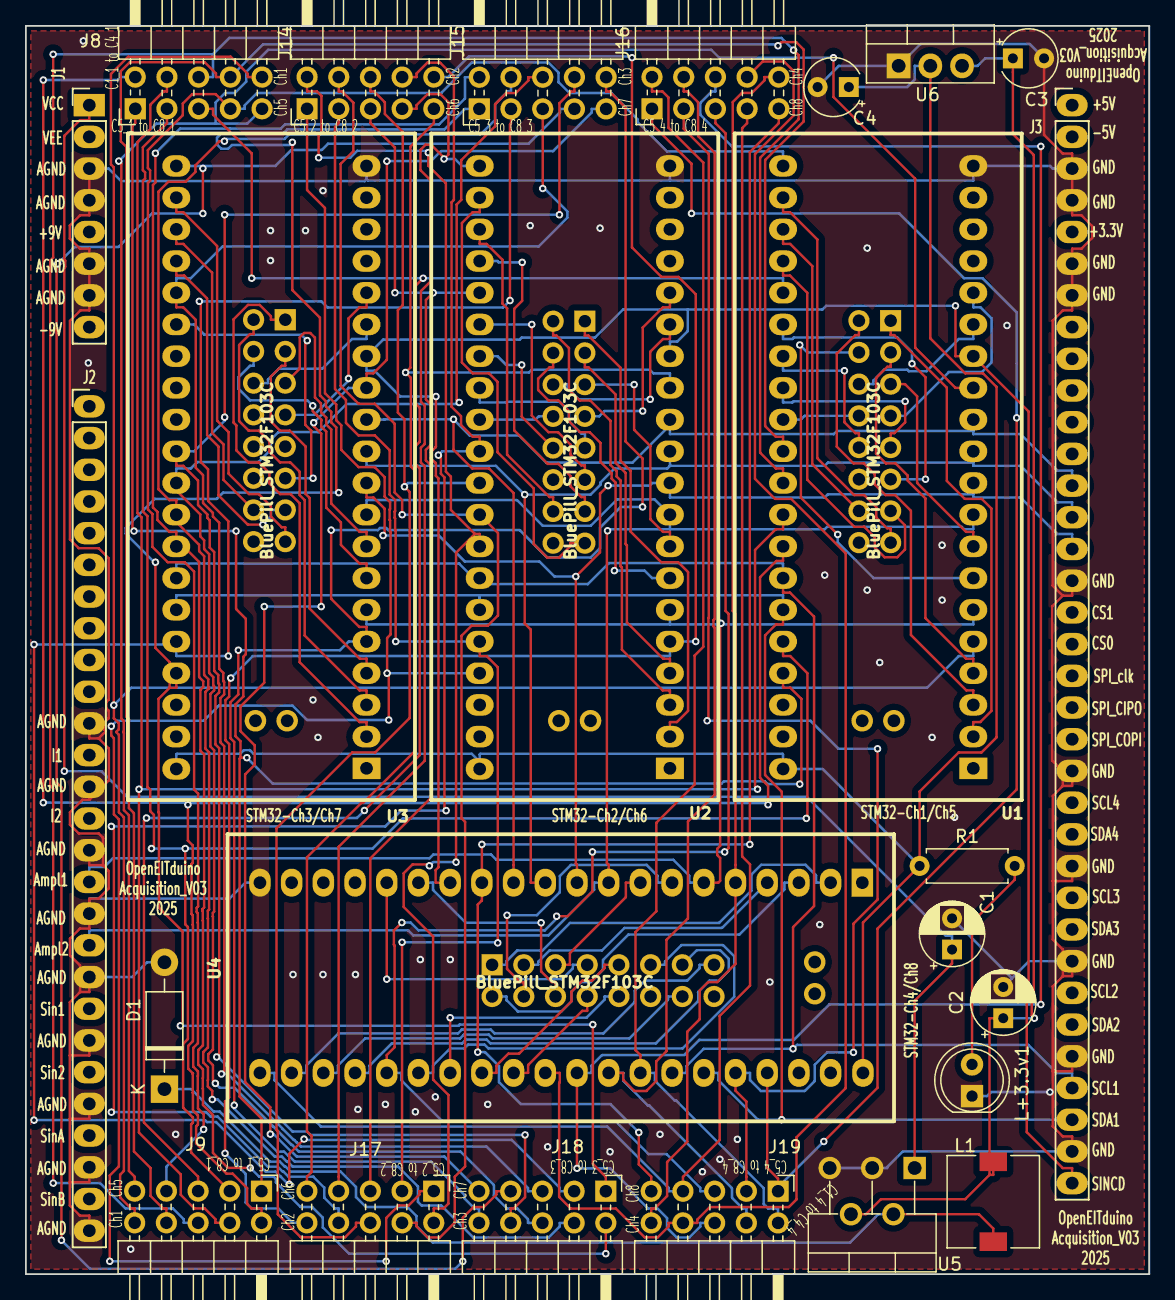
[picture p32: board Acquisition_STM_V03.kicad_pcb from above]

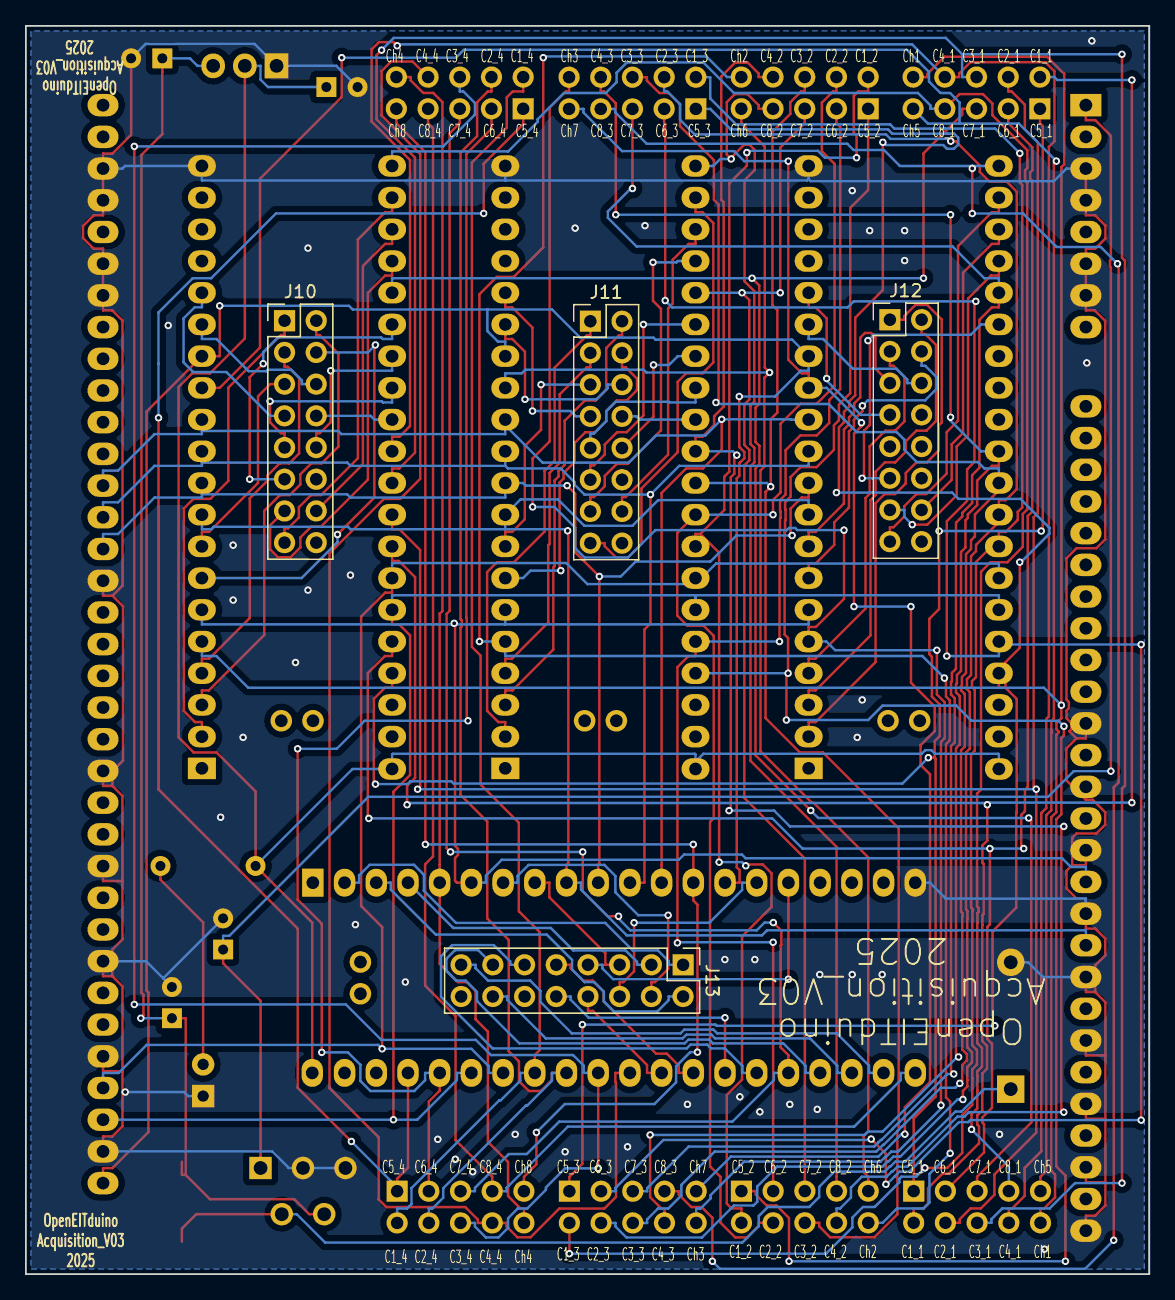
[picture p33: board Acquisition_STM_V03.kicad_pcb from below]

Board: 2 copper layers, 90.0 x 100.0 mm, 29 parts (4 on the bottom side), 107 nets.

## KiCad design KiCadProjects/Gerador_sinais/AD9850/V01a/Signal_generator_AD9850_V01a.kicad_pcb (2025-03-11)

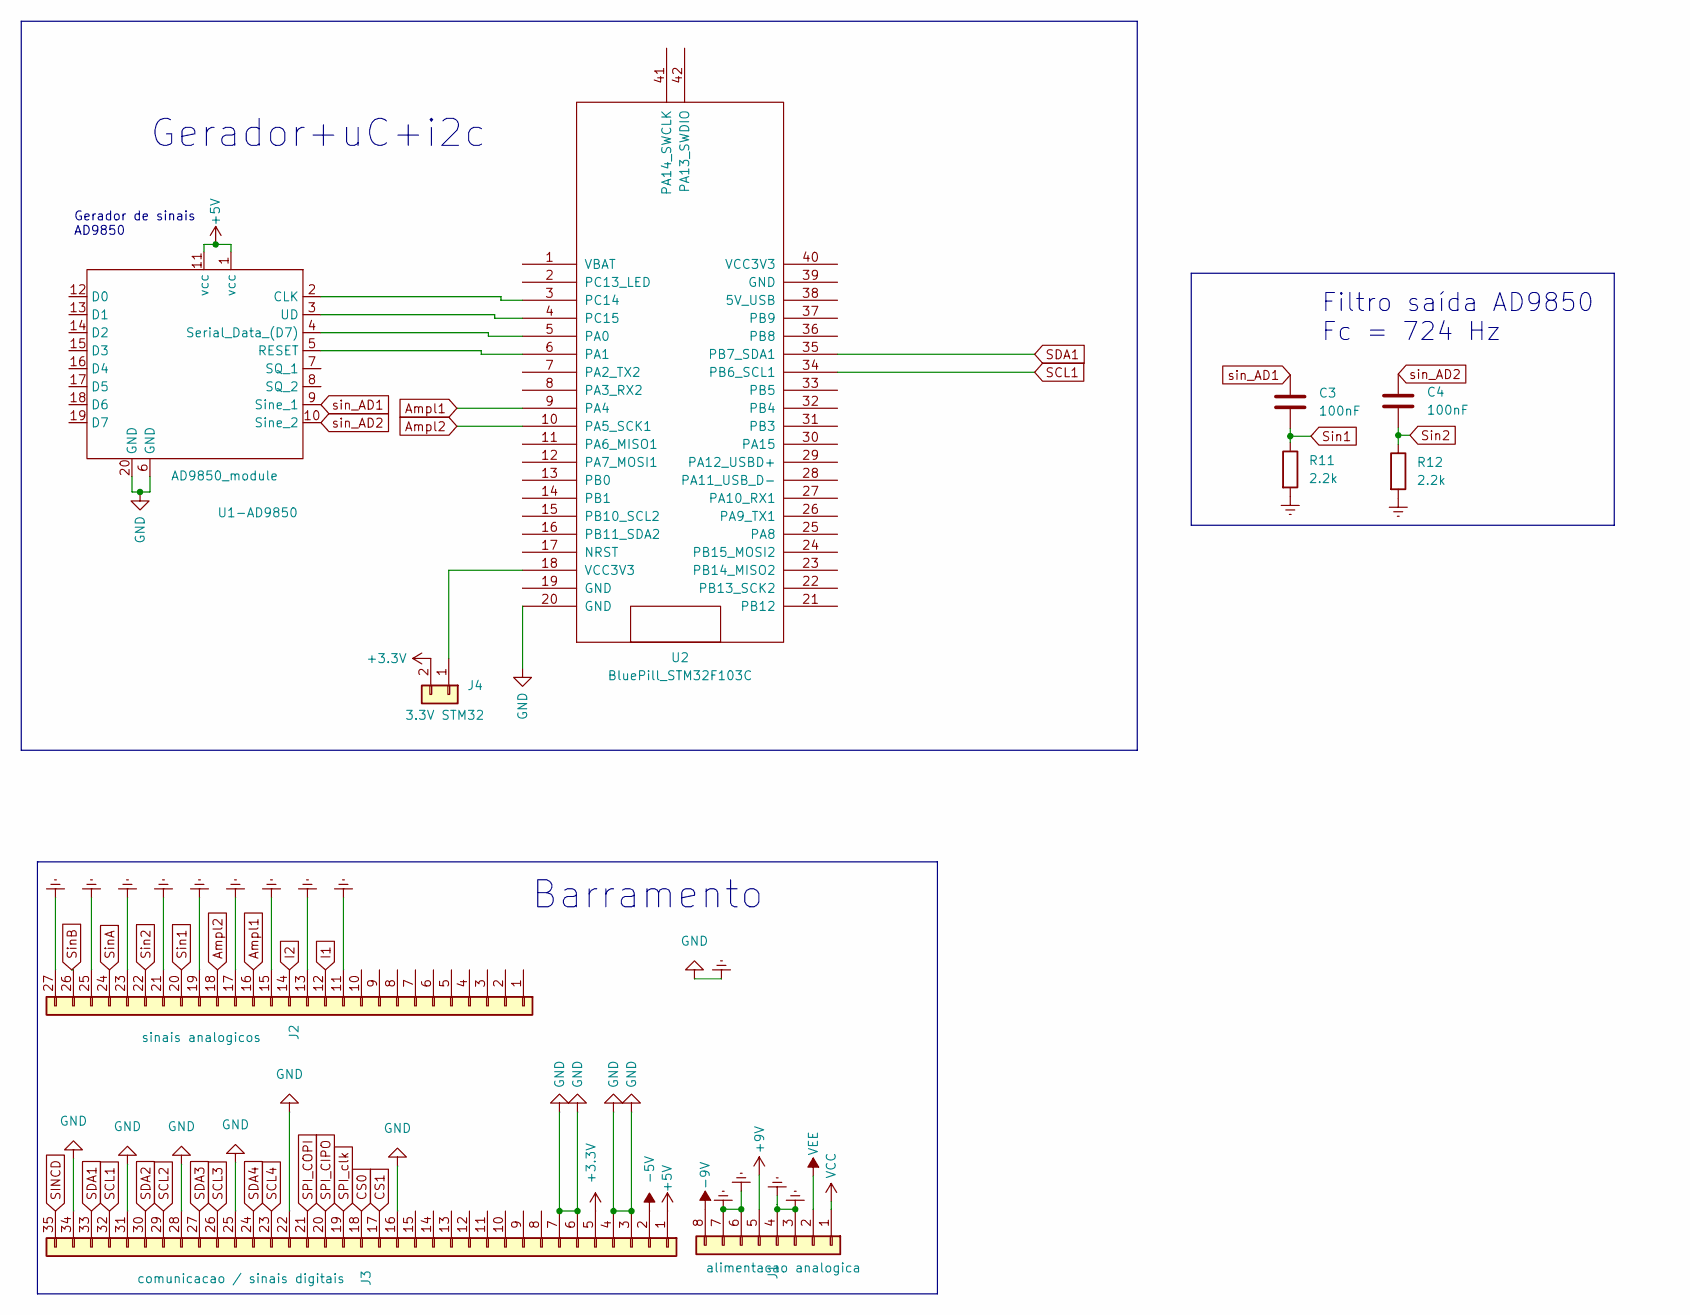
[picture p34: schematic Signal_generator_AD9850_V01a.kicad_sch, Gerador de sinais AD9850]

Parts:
C3, C4: 100nF; C_Disc_D3.0mm_W1.6mm_P2.50mm
J1: alimentacao analogica; PinHeader_1x08_P2.54mm_Vertical
J2: sinais analogicos; PinHeader_1x27_P2.54mm_Vertical
J3: comunicacao / sinais digitais; PinHeader_1x35_P2.54mm_Vertical
J4: 3.3V STM32; PinHeader_1x02_P2.54mm_Vertical
R11, R12: 2.2k; R_Axial_DIN0207_L6.3mm_D2.5mm_P7.62mm_Horizontal
U1-AD9850: AD9850_module
U2: BluePill_STM32F103C

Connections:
+3.3V: J3.5, J4.2
+5V: J3.1, U1-AD9850.1 (vcc), U1-AD9850.11 (vcc)
+9V: J1.5
-5V: J3.2
-9V: J1.8
Ampl1: J2.16, U2.9 (PA4)
Ampl2: J2.18, U2.10 (PA5_SCK1)
CS0: J3.18
CS1: J3.17
Earth: J1.3, J1.4, J1.6, J1.7, J2.11, J2.13, J2.15, J2.17, J2.19, J2.21, J2.23, J2.25, J2.27, J3.3, J3.4, J3.6, J3.7, J3.16, J3.22, J3.25, J3.28, J3.31, J3.34, R11.2, R12.2, U1-AD9850.6 (GND), U1-AD9850.20 (GND), U2.20 (GND)
I1: J2.12
I2: J2.14
unnamed: J4.1, U2.18 (VCC3V3)
unnamed: U1-AD9850.2 (CLK), U2.3 (PC14)
unnamed: U1-AD9850.5 (RESET), U2.6 (PA1)
unnamed: U1-AD9850.4 (Serial_Data_(D7)), U2.5 (PA0)
unnamed: U1-AD9850.3 (UD), U2.4 (PC15)
SCL1: J3.32, U2.34 (PB6_SCL1)
SCL2: J3.29
SCL3: J3.26
SCL4: J3.23
SDA1: J3.33, U2.35 (PB7_SDA1)
SDA2: J3.30
SDA3: J3.27
SDA4: J3.24
SINCD: J3.35
SPI_CIPO: J3.20
SPI_COPI: J3.21
SPI_clk: J3.19
Sin1: C3.2, J2.20, R11.1
Sin2: C4.2, J2.22, R12.1
SinA: J2.24
SinB: J2.26
VCC: J1.1
VEE: J1.2
sin_AD1: C3.1, U1-AD9850.9 (Sine_1)
sin_AD2: C4.1, U1-AD9850.10 (Sine_2)

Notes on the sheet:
Gerador+uC+i2c
Filtro saída AD9850 Fc = 724 Hz
Gerador de sinais AD9850
Barramento

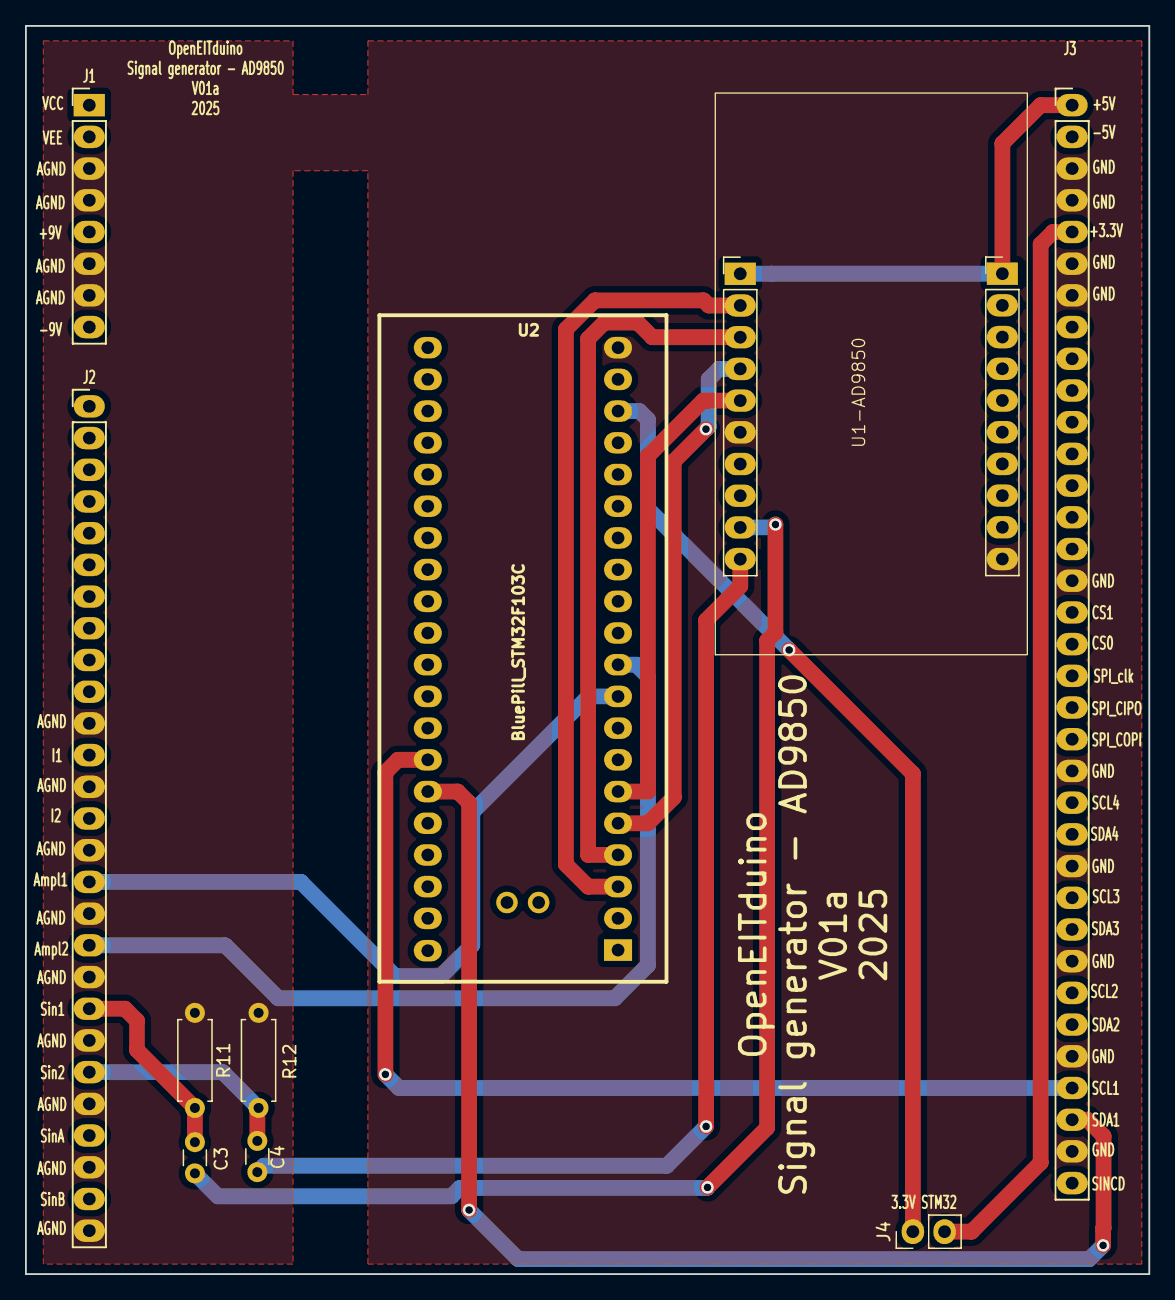
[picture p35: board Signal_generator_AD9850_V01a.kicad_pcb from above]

Board: 2 copper layers, 90.0 x 100.0 mm, 10 parts (0 on the bottom side), 16 nets.

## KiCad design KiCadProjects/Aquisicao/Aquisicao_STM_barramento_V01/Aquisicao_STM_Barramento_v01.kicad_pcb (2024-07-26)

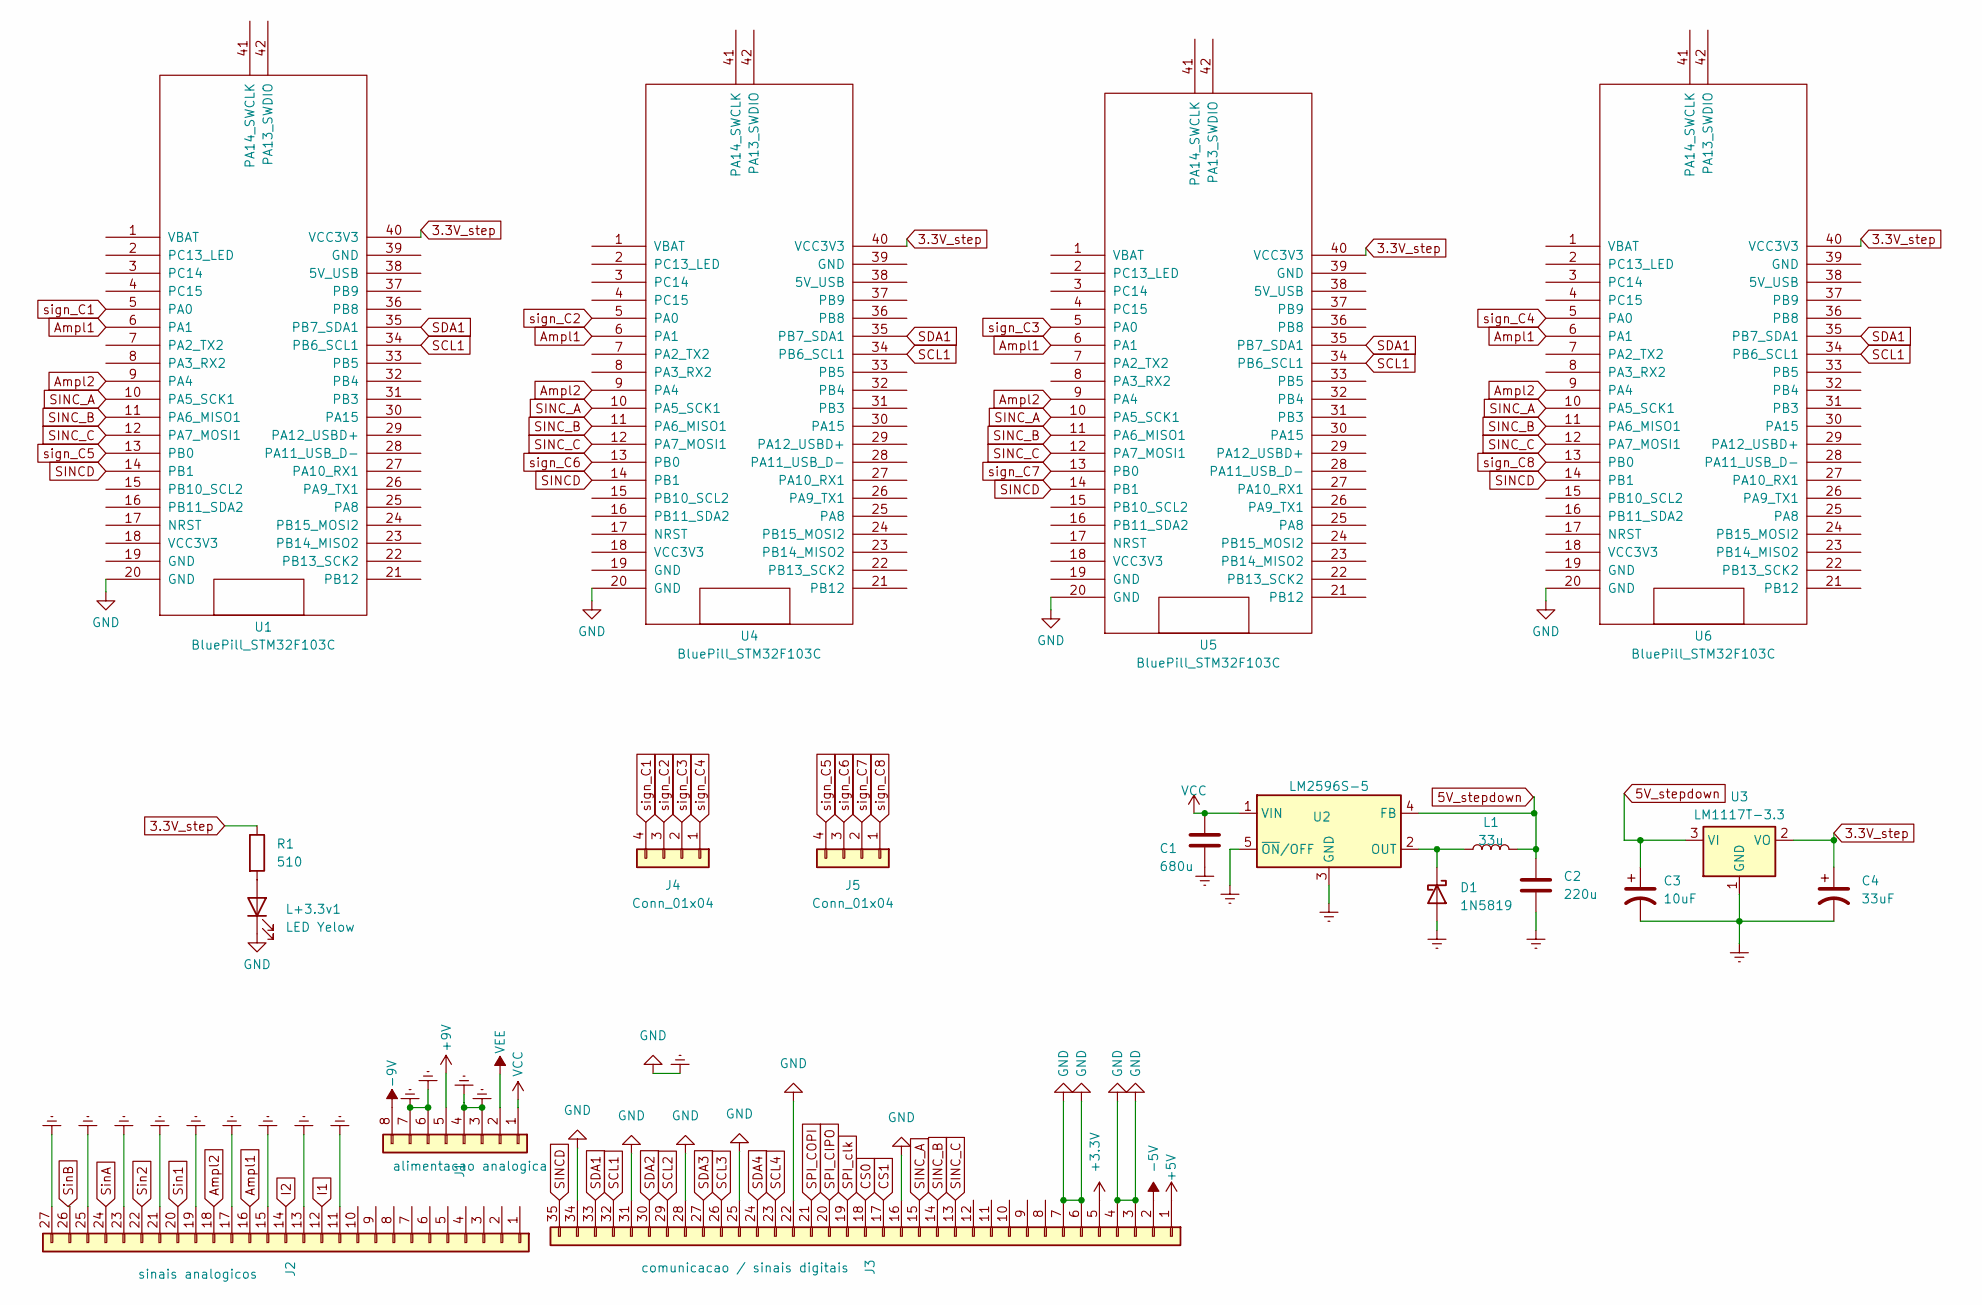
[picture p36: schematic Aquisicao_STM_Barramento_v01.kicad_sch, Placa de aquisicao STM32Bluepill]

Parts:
C1: 680u; CP_Radial_D5.0mm_P2.50mm
C2: 220u; CP_Radial_D5.0mm_P2.50mm
C3: 10uF; CP_Radial_Tantal_D4.5mm_P2.50mm
C4: 33uF; CP_Radial_Tantal_D4.5mm_P2.50mm
D1: 1N5819; D_DO-41_SOD81_P10.16mm_Horizontal
J1: alimentacao analogica; PinHeader_1x08_P2.54mm_Vertical
J2: sinais analogicos; PinHeader_1x27_P2.54mm_Vertical
J3: comunicacao / sinais digitais; PinHeader_1x35_P2.54mm_Vertical
J4, J5: Conn_01x04; PinHeader_1x04_P2.54mm_Horizontal
L1: 33u; L_7.3x7.3_H4.5
L+3.3v1: LED Yelow; LED_D5.0mm
R1: 510; R_Axial_DIN0207_L6.3mm_D2.5mm_P7.62mm_Horizontal
U1, U4, U5, U6: BluePill_STM32F103C
U2: LM2596S-5; TO-220-5_P3.4x3.7mm_StaggerOdd_Lead3.8mm_Vertical
U3: LM1117T-3.3; TO-220-3_Vertical

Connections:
3.3V_step: C4.1, R1.1, U1.40 (VCC3V3), U3.2 (VO), U4.40 (VCC3V3), U5.40 (VCC3V3), U6.40 (VCC3V3)
5V_stepdown: C2.1, C3.1, L1.2, U2.4 (FB), U3.3 (VI)
+3.3V: J3.5
+5V: J3.1
+9V: J1.5
-5V: J3.2
-9V: J1.8
Ampl1: J2.16, U1.6 (PA1), U4.6 (PA1), U5.6 (PA1), U6.6 (PA1)
Ampl2: J2.18, U1.9 (PA4), U4.9 (PA4), U5.9 (PA4), U6.9 (PA4)
CS0: J3.18
CS1: J3.17
Earth: C1.2, C2.2, C3.2, C4.2, D1.2 (A), J1.3, J1.4, J1.6, J1.7, J2.11, J2.13, J2.15, J2.17, J2.19, J2.21, J2.23, J2.25, J2.27, J3.3, J3.4, J3.6, J3.7, J3.16, J3.22, J3.25, J3.28, J3.31, J3.34, L+3.3v1.1 (K), U1.20 (GND), U2.3 (GND), U2.5 (~ON/OFF), U3.1 (GND), U4.20 (GND), U5.20 (GND), U6.20 (GND)
I1: J2.12
I2: J2.14
unnamed: D1.1 (K), L1.1, U2.2 (OUT)
unnamed: L+3.3v1.2 (A), R1.2
SCL1: J3.32, U1.34 (PB6_SCL1), U4.34 (PB6_SCL1), U5.34 (PB6_SCL1), U6.34 (PB6_SCL1)
SCL2: J3.29
SCL3: J3.26
SCL4: J3.23
SDA1: J3.33, U1.35 (PB7_SDA1), U4.35 (PB7_SDA1), U5.35 (PB7_SDA1), U6.35 (PB7_SDA1)
SDA2: J3.30
SDA3: J3.27
SDA4: J3.24
SINCD: J3.35, U1.14 (PB1), U4.14 (PB1), U5.14 (PB1), U6.14 (PB1)
SINC_A: J3.15, U1.10 (PA5_SCK1), U4.10 (PA5_SCK1), U5.10 (PA5_SCK1), U6.10 (PA5_SCK1)
SINC_B: J3.14, U1.11 (PA6_MISO1), U4.11 (PA6_MISO1), U5.11 (PA6_MISO1), U6.11 (PA6_MISO1)
SINC_C: J3.13, U1.12 (PA7_MOSI1), U4.12 (PA7_MOSI1), U5.12 (PA7_MOSI1), U6.12 (PA7_MOSI1)
SPI_CIPO: J3.20
SPI_COPI: J3.21
SPI_clk: J3.19
Sin1: J2.20
Sin2: J2.22
SinA: J2.24
SinB: J2.26
VCC: C1.1, J1.1, U2.1 (VIN)
VEE: J1.2
sign_C1: J4.4, U1.5 (PA0)
sign_C2: J4.3, U4.5 (PA0)
sign_C3: J4.2, U5.5 (PA0)
sign_C4: J4.1, U6.5 (PA0)
sign_C5: J5.4, U1.13 (PB0)
sign_C6: J5.3, U4.13 (PB0)
sign_C7: J5.2, U5.13 (PB0)
sign_C8: J5.1, U6.13 (PB0)

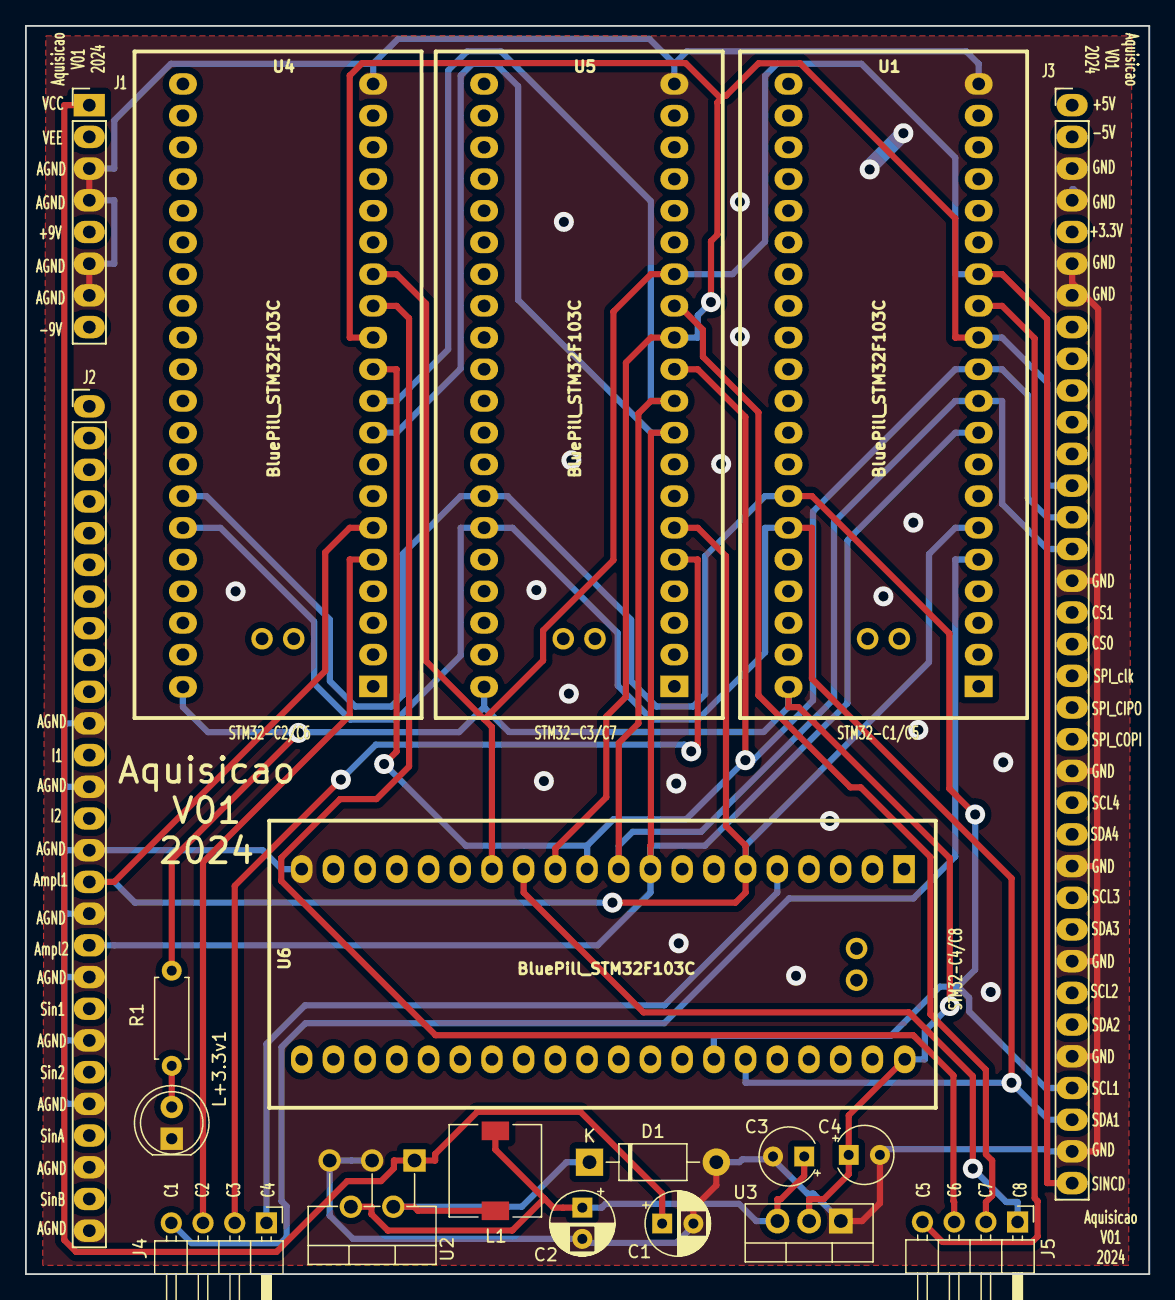
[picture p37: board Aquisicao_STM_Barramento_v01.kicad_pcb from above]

Board: 2 copper layers, 90.0 x 100.0 mm, 19 parts (0 on the bottom side), 22 nets.

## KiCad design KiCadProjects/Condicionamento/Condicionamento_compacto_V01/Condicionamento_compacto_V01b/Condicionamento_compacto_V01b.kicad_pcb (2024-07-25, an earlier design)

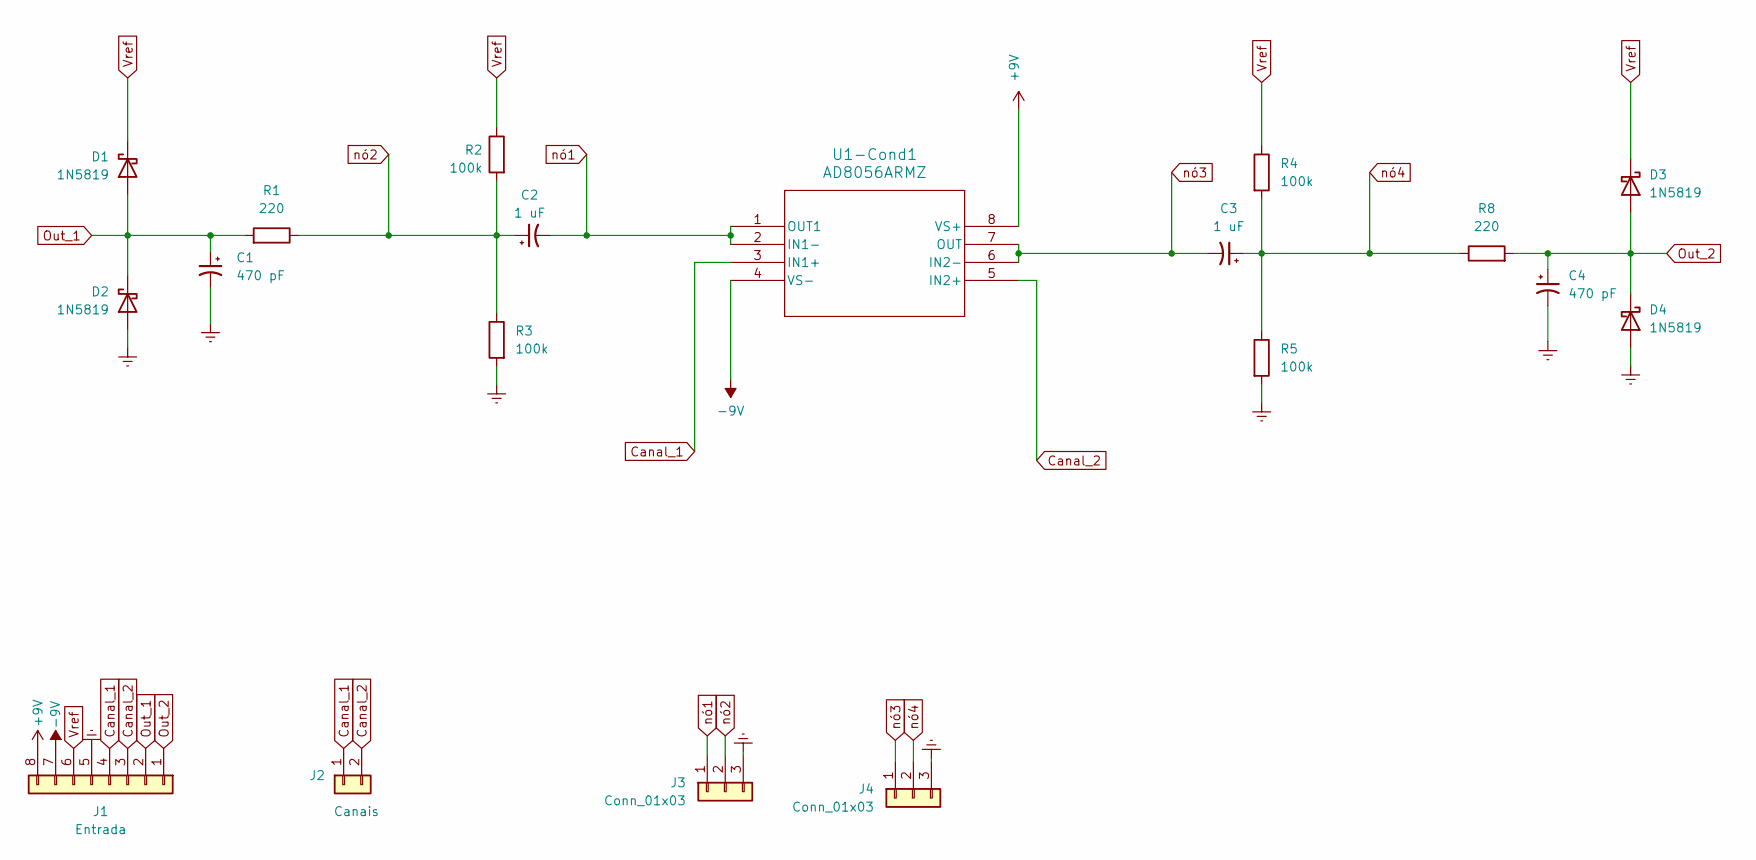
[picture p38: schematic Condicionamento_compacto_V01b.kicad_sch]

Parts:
C1, C4: 470 pF; CP_Radial_D5.0mm_P2.50mm
C2, C3: 1 uF; CP_Radial_D5.0mm_P2.50mm
D1, D2, D3, D4: 1N5819; D_DO-41_SOD81_P10.16mm_Horizontal
J1: Entrada; PinSocket_1x08_P2.54mm_Vertical
J2: Canais; PinHeader_1x02_P2.54mm_Vertical
J3, J4: Conn_01x03; PinHeader_1x03_P2.54mm_Vertical
R1, R8: 220; R_Axial_DIN0207_L6.3mm_D2.5mm_P7.62mm_Horizontal
R2, R3, R4, R5: 100k; R_Axial_DIN0207_L6.3mm_D2.5mm_P7.62mm_Horizontal
U1-Cond1: AD8056ARMZ; RM_8_ADI

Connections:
+9V: J1.8, U1-Cond1.8 (VS+)
-9V: J1.7, U1-Cond1.4 (VS-)
Canal_1: J1.4, J2.1, U1-Cond1.3 (IN1+)
Canal_2: J1.3, J2.2, U1-Cond1.5 (IN2+)
Earth: C1.2, C4.2, D2.2 (A), D4.2 (A), J1.5, J3.3, J4.3, R3.2, R5.2
Out_1: C1.1, D1.2 (A), D2.1 (K), J1.2, R1.2
Out_2: C4.1, D3.2 (A), D4.1 (K), J1.1, R8.2
Vref: D1.1 (K), D3.1 (K), J1.6, R2.1, R4.1
nó1: C2.2, J3.1, U1-Cond1.1 (OUT1), U1-Cond1.2 (IN1-)
nó2: C2.1, J3.2, R1.1, R2.2, R3.1
nó3: C3.2, J4.1, U1-Cond1.6 (IN2-), U1-Cond1.7 (OUT)
nó4: C3.1, J4.2, R4.2, R5.1, R8.1


Board: 2 copper layers, 45.0 x 25.0 mm, 19 parts (0 on the bottom side), 12 nets.

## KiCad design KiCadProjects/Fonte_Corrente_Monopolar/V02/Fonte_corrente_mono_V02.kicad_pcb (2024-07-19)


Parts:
C3: 1 uF; CP_Radial_D5.0mm_P2.50mm
C4: 470 pF; CP_Radial_D5.0mm_P2.50mm
D1, D2: 1N5819; D_DO-41_SOD81_P10.16mm_Horizontal
J1: alimentacao analogica; PinHeader_1x08_P2.54mm_Vertical
J2: sinais analogicos; PinHeader_1x27_P2.54mm_Vertical
J3: comunicacao / sinais digitais; PinHeader_1x35_P2.54mm_Vertical
J4: signal select; PinHeader_1x03_P2.54mm_Vertical
J7: +3.3V | +5.0V; PinHeader_1x03_P2.54mm_Vertical
L+3.3v1: LED - Yelow; LED_D5.0mm
L+5v1: LED - Green; LED_D5.0mm
L+9v1: LED - Blue; LED_D5.0mm
L-9v1: LED - Red; LED_D5.0mm
R1, R2, R3, R5, R10, R11: 100k; R_Axial_DIN0207_L6.3mm_D2.5mm_P7.62mm_Horizontal
R4, R6: 1k; R_Axial_DIN0207_L6.3mm_D2.5mm_P7.62mm_Horizontal
R7, R13: 1.5k; R_Axial_DIN0207_L6.3mm_D2.5mm_P7.62mm_Horizontal
R8: 470; R_Axial_DIN0207_L6.3mm_D2.5mm_P7.62mm_Horizontal
R9: 510; R_Axial_DIN0207_L6.3mm_D2.5mm_P7.62mm_Horizontal
R12: 220; R_Axial_DIN0207_L6.3mm_D2.5mm_P7.62mm_Horizontal
Rganho-I1: 3,3k; R_Axial_DIN0207_L6.3mm_D2.5mm_P7.62mm_Horizontal
RpSCL1, RpSCL2, RpSCL3, RpSCL4: 4k7; R_Axial_DIN0207_L6.3mm_D2.5mm_P7.62mm_Horizontal
RpSDA1, RpSDA2, RpSDA3, RpSDA4: 4k7; R_Axial_DIN0207_L6.3mm_D2.5mm_P7.62mm_Horizontal
Rsentinela-I1: 10; R_Axial_DIN0207_L6.3mm_D2.5mm_P7.62mm_Horizontal
U1-howland1, U3-cond1: AD828AN; AD828
U2-INA-I1: INA128; DIP-8_W7.62mm

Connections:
+3.3V: J3.5, J7.1, R9.1, RpSCL1.2, RpSCL3.2, RpSDA1.2, RpSDA3.2
+5V: J3.1, J7.3, R8.1, RpSCL2.1, RpSCL4.1, RpSDA2.1, RpSDA4.1
+9V: J1.5, R13.1, U1-howland1.8 (V+), U2-INA-I1.7 (V+), U3-cond1.8 (V+)
-5V: J3.2
-9V: J1.8, R7.1, U1-howland1.4 (V-), U2-INA-I1.4 (V-), U3-cond1.4 (V-)
Ampl1: C4.1, D1.2 (A), D2.1 (K), J2.16, R12.2
Ampl2: J2.18
CS0: J3.18
CS1: J3.17
Earth: C4.2, D2.2 (A), J1.3, J1.4, J1.6, J1.7, J2.11, J2.13, J2.15, J2.17, J2.19, J2.21, J2.23, J2.25, J2.27, J3.3, J3.4, J3.6, J3.7, J3.16, J3.22, J3.25, J3.28, J3.31, J3.34, L+3.3v1.1 (K), L+5v1.1 (K), L+9v1.1 (K), L-9v1.2 (A), R4.2, R11.2, U2-INA-I1.5 (Ref)
I1: J2.12, Rsentinela-I1.2, U2-INA-I1.2 (-)
I2: J2.14
unnamed: D1.1 (K), J7.2, R10.1
unnamed: J4.2, U1-howland1.3 (+IN1)
unnamed: L+3.3v1.2 (A), R9.2
unnamed: L+5v1.2 (A), R8.2
unnamed: L+9v1.2 (A), R13.2
unnamed: L-9v1.1 (K), R7.2
unnamed: R3.2, R4.1
unnamed: Rganho-I1.1, U2-INA-I1.1 (Rg)
unnamed: Rganho-I1.2, U2-INA-I1.8 (Rg)
unnamed: R3.1, R5.1, U1-howland1.5 (+IN2)
unnamed: R1.1, R2.1, U1-howland1.6 (-IN2)
unnamed: R2.2, R6.1, U1-howland1.7 (OUT2)
SCL1: J3.32, RpSCL1.1
SCL2: J3.29, RpSCL2.2
SCL3: J3.26, RpSCL3.1
SCL4: J3.23, RpSCL4.2
SDA1: J3.33, RpSDA1.1
SDA2: J3.30, RpSDA2.2
SDA3: J3.27, RpSDA3.1
SDA4: J3.24, RpSDA4.2
SINCD: J3.35
SPI_CIPO: J3.20
SPI_COPI: J3.21
SPI_clk: J3.19
Sin1: J2.20, J4.3
Sin2: J2.22
SinA: J2.24, J4.1
SinB: J2.26
VCC: J1.1
VEE: J1.2
V_INA: U2-INA-I1.6, U3-cond1.5 (+IN2)
nó1: C3.2, U3-cond1.6 (-IN2), U3-cond1.7 (OUT2)
nó2: C3.1, R10.2, R11.1, R12.1
out_buffer: R1.2, U1-howland1.1 (OUT1), U1-howland1.2 (-IN1)
out_corrente: R5.2, R6.2, Rsentinela-I1.1, U2-INA-I1.3 (+)

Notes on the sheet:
Fonte de corrente / INA
Iled => 5mA Vled ~ 3V
Condicionamento


Board: 2 copper layers, 90.0 x 100.0 mm, 39 parts (0 on the bottom side), 34 nets.

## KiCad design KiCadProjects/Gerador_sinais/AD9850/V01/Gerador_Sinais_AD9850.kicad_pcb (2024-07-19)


Board: 2 copper layers, 90.0 x 100.0 mm, 42 parts (0 on the bottom side), 60 nets.

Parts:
C1, C2, C3, C4, C5, C6: 100nF; C_Disc_D3.0mm_W1.6mm_P2.50mm
J1: alimentacao analogica; PinHeader_1x08_P2.54mm_Vertical
J2: sinais analogicos; PinHeader_1x27_P2.54mm_Vertical
J3: comunicacao / sinais digitais; PinHeader_1x35_P2.54mm_Vertical
J4: 3.3V STM32; PinHeader_1x02_P2.54mm_Vertical
J5: 5.0V STM32; PinHeader_1x02_P2.54mm_Vertical
J6: Select SinA; PinHeader_1x03_P2.54mm_Vertical
J7: Select SinB; PinHeader_1x03_P2.54mm_Vertical
J8: Squad_wave; PinHeader_1x03_P2.54mm_Vertical
J9: Encoder KY-040; PinHeader_1x05_P2.54mm_Vertical
J10: teclado matricial; PinHeader_1x08_P2.54mm_Horizontal
J11: botoes_selecao; PinHeader_1x05_P2.54mm_Horizontal
L+3.3v1: LED - Yelow; LED_D5.0mm
L+5v1: LED Green; LED_D5.0mm
L+9v1: LED Blue; LED_D5.0mm
L-9v1: LED Red; LED_D5.0mm
R1, R2: 1.5k; R_Axial_DIN0207_L6.3mm_D2.5mm_P7.62mm_Horizontal
R3: 470; R_Axial_DIN0207_L6.3mm_D2.5mm_P7.62mm_Horizontal
R4: 510; R_Axial_DIN0207_L6.3mm_D2.5mm_P7.62mm_Horizontal
R5, R6: 51k; R_Axial_DIN0207_L6.3mm_D2.5mm_P7.62mm_Horizontal
R7, R8: 4k7; R_Axial_DIN0207_L6.3mm_D2.5mm_P7.62mm_Horizontal
R9, R10, R11, R12, R13, R14: 160k; R_Axial_DIN0207_L6.3mm_D2.5mm_P7.62mm_Horizontal
U1-AD9850: AD9850_module
U2: BluePill_STM32F103C
U3-ganho1, U6-filtro-saida1, U7-bufferAD9850: AD828AN; AD828
U4-DigPot2, U5-DigPot1: X9c10x; X9c10X_module

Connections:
+3.3V: J3.5, J4.2, R4.1, R7.2, R8.2
+5V: J3.1, J5.1, J9.4, R3.1, U1-AD9850.1 (vcc), U1-AD9850.11 (vcc), U4-DigPot2.1 (VCC), U4-DigPot2.10 (VCC), U5-DigPot1.1 (VCC), U5-DigPot1.10 (VCC)
+9V: J1.5, R1.1, U3-ganho1.8 (V+), U6-filtro-saida1.8 (V+), U7-bufferAD9850.8 (V+)
-9V: J1.8, R2.1, U3-ganho1.4 (V-), U6-filtro-saida1.4 (V-), U7-bufferAD9850.4 (V-)
Ampl1: J2.16, U2.9 (PA4)
Ampl2: J2.18, U2.10 (PA5_SCK1)
Down_gain: J11.2, U2.25 (PA8)
Earth: J1.3, J1.4, J1.6, J1.7, J2.11, J2.13, J2.15, J2.17, J2.19, J2.21, J2.23, J2.25, J2.27, J3.3, J3.4, J3.6, J3.7, J3.16, J3.22, J3.25, J3.28, J3.31, J3.34, J8.3, J9.5, J11.1, L+3.3v1.1 (K), L+5v1.1 (K), L+9v1.1 (K), L-9v1.2 (A), R9.2, R10.2, R11.2, R12.2, R13.2, R14.2, U1-AD9850.6 (GND), U1-AD9850.20 (GND), U2.20 (GND), U3-ganho1.3 (+IN1), U3-ganho1.5 (+IN2), U4-DigPot2.2 (GND), U4-DigPot2.6 (GND), U5-DigPot1.2 (GND), U5-DigPot1.6 (GND)
En1: J9.1, U2.30 (PA15)
En2: J9.2, U2.36 (PB8)
En3: J9.3, U2.37 (PB9)
M1: J10.1, U2.7 (PA2_TX2)
M2: J10.2, U2.8 (PA3_RX2)
M3: J10.3, U2.29 (PA12_USBD+)
M4: J10.4, U2.28 (PA11_USB_D-)
M5: J10.5, U2.11 (PA6_MISO1)
M6: J10.6, U2.12 (PA7_MOSI1)
M7: J10.7, U2.13 (PB0)
M8: J10.8, U2.21 (PB12)
unnamed: J4.1, U2.18 (VCC3V3)
unnamed: J5.2, U2.38 (5V_USB)
unnamed: L+3.3v1.2 (A), R4.2
unnamed: L+5v1.2 (A), R3.2
unnamed: L+9v1.2 (A), R1.2
unnamed: L-9v1.1 (K), R2.2
unnamed: U1-AD9850.2 (CLK), U2.3 (PC14)
unnamed: U1-AD9850.5 (RESET), U2.6 (PA1)
unnamed: U1-AD9850.4 (Serial_Data_(D7)), U2.5 (PA0)
unnamed: U1-AD9850.3 (UD), U2.4 (PC15)
unnamed: R6.1, U3-ganho1.2 (-IN1), U5-DigPot1.8 (RW), U5-DigPot1.9 (RH)
unnamed: R5.1, U3-ganho1.6 (-IN2), U4-DigPot2.8 (RW), U4-DigPot2.9 (RH)
unnamed: C1.2, R9.1, U6-filtro-saida1.3 (+IN1)
unnamed: C2.2, R10.1, U6-filtro-saida1.5 (+IN2)
Pot1_CS_(X9c104): U2.14 (PB1), U5-DigPot1.5 (CS)
Pot1_X9c10x_INC: U2.16 (PB11_SDA2), U5-DigPot1.3 (INC)
Pot1_X9c10x_U/D: U2.15 (PB10_SCL2), U5-DigPot1.4 (U/D)
Pot2_CS_(X9c104): U2.33 (PB5), U4-DigPot2.5 (CS)
Pot2_X9c10x_INC: U2.31 (PB3), U4-DigPot2.3 (INC)
Pot2_X9c10x_U/D: U2.32 (PB4), U4-DigPot2.4 (U/D)
SCL1: J3.32, R8.1, U2.34 (PB6_SCL1)
SDA1: J3.33, R7.1, U2.35 (PB7_SDA1)
SQ1: C5.2, J8.2, R13.1
SQ2: C6.2, J8.1, R14.1
SQ_AD1: C5.1, U1-AD9850.7 (SQ_1)
SQ_AD2: C6.1, U1-AD9850.8 (SQ_2)
Sin1: J2.20, U5-DigPot1.7 (RL), U7-bufferAD9850.1 (OUT1), U7-bufferAD9850.2 (-IN1)
Sin1_PA: C3.2, R11.1, U7-bufferAD9850.3 (+IN1)
Sin1_filter: J6.1, U6-filtro-saida1.1 (OUT1), U6-filtro-saida1.2 (-IN1)
Sin1_gain: C1.1, J6.3, R6.2, U3-ganho1.1 (OUT1)
Sin2: J2.22, U4-DigPot2.7 (RL), U7-bufferAD9850.6 (-IN2), U7-bufferAD9850.7 (OUT2)
Sin2_PA: C4.2, R12.1, U7-bufferAD9850.5 (+IN2)
Sin2_filter: J7.1, U6-filtro-saida1.6 (-IN2), U6-filtro-saida1.7 (OUT2)
Sin2_gain: C2.1, J7.3, R5.2, U3-ganho1.7 (OUT2)
SinA: J2.24, J6.2
SinB: J2.26, J7.2
Up_gain: J11.3, U2.24 (PB15_MOSI2)
freq+: J11.5, U2.22 (PB13_SCK2)
freq-: J11.4, U2.23 (PB14_MISO2)
sin_AD1: C3.1, U1-AD9850.9 (Sine_1)
sin_AD2: C4.1, U1-AD9850.10 (Sine_2)

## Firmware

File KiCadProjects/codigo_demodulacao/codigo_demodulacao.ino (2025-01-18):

/* 
 * Exemplo de uso do ADC do STM32F103 em Dual Mode.
 *  
 * A taxa de amostragem é dada por:
 *  FS = 72 MHz / prescaler / (ADC_SMPR + 12.5)
 *  
 * Para PRE_SCALER==RCC_ADCPRE_PCLK_DIV_6 e ADC_SMPR==ADC_SMPR_7_5, a taxa de amostragem é:
 *  - Regular simultaneous mode: 600 kSps por canal, no caso de 2 canais
 *  - Fast interleaved mode: 1200 kSps
 *  
 * Obs: segundo nota do Reference Manual ([1], pág 215), não deve ser usado prescaler menor que 6 (72MHz/6 = 12MHz):
 * "The ADC input clock is generated from the PCLK2 clock divided by a prescaler and it must not exceed 14 MHz"
 * Provavelmente, a precisão da medida cai em frequências mais altas e cargas de alta impedância de saída devido aos 
 * capacitores do ADC (ADC do tipo "successive approximation analog-to-digital converter"). Ver [5], págs 6 e 33.
 *  
 * Escrito por: Erick León
 * 
 * Referências:
 * 
 * [1] STM32F10xxx Reference Manual (RM0008), disponível em www.st.com;
 * [2] Application note (AN3116), STM32's ADC modes and theis applications, disponível em www.st.com;
 * [3] Problems with regular simultaneous dual ADC conversion with DMA transfer, Spark Logic Forum,
 * disponível em https://sparklogic.ru/arduino-for-stm32/problems-with-regular-simultaneous-dual-adc.html
 * [4] https://github.com/rogerclarkmelbourne/Arduino_STM32/blob/master/STM32F1/libraries/STM32ADC/src/STM32ADC.cpp
 * [5] Application note (AN2834), How to get the best ADC accuracy in STM32 microcontrollers, disponível em www.st.com;

 * 
 */

#include <Wire_slave.h>
#include "stm32_adc_dual_mode.h"
#include "dft.h"


//#define comfase


#if defined comfase
       //
#else
       //
#endif



int npontos_base; // menor mutiplo inteiro de 'sample_freq/freq_sinal'.
//Define a quantidade minima de pontos para reconstruir o menor numero possivel de ciclos do sinal.
int n_pontos_mult;// fator multiplicador de 'npontos_base'. Permite adquirir mais ciclos do sinal.

const float referenceVolts= 3.3;
float sample_freq =  (72e6 / 6.0 / 20.0); // = 600kHz
float freq_sinal = 50000;  // 50kHz
float phase1, phase2, amplit1, amplit2; //phase1: phase2: amplit1: amplit2:
int NUM_SAMPLES = 24;      // number of samples for each ADCx. Each channel will be sampled NUM_SAMPLES/CHANNELS_PER_ADC
//NUM_SAMPLES precisa apenas ser iniciada????????? pode ser qualquer valor??????????
byte comando = 0; //entrada do i2c
boolean mediu = false;

int tempo_demodulacao ; // tempo em ms que demora a leitura e demodulacao



#define CHANNELS_PER_ADC  1                      // number of channels for each ADC. Must match values in ADCx_Sequence array below
#define ADC_SMPR          ADC_SMPR_7_5           // when using dual mode, each pair of channels must have same rate. Here all channels have the same
#define NUM_SAMPLES_MAX   500                    // number of samples for each ADCx. Each channel will be sampled NUM_SAMPLES/CHANNELS_PER_ADC
#define PRE_SCALER        RCC_ADCPRE_PCLK_DIV_6  // Prescaler do ADC
#define FAST_INTERLEAVED  false                  // Fast Interleave Mode Flag. Para "dobrar" taxa de amostragem medindo o mesmo canal dos 2 ADCs.
                                                 // Se 'false', habilita "Regular simultaneous mode". Se 'true', habilita "Fast interleaved mode".

#define LED PC13

uint32 adcbuf[NUM_SAMPLES_MAX+1];  // buffer to hold samples, ADC1 16bit, ADC2 16 bit
uint16_t datav1[NUM_SAMPLES_MAX+1];
uint16_t datav2[NUM_SAMPLES_MAX+1];

// O STM32F103 possui 10 pinos do ADC disponíveis:
// pino A0 (PA0) -> 0 (ADC0)
// ...
// pino A7 (PA7) -> 7 (ADC7)
// pino B0 (PB0) -> 8 (ADC8)
// pino B1 (PB1) -> 9 (ADC9)
// Para "dobrar" taxa de amostragem (FAST_INTERLEAVED true), medir o mesmo canal dos 2 ADCs.

//uint8 ADC1_Sequence[]={8,0,0,0,0,0};   // ADC1 channels sequence, left to right. Unused values must be 0. Note that these are ADC /channels, not pins
//uint8 ADC2_Sequence[]={9,0,0,0,0,0};   // ADC2 channels sequence, left to right. Unused values must be 0

// CASO 1: lê canal X e amplitude I1
uint8 ADC1_Sequence[]={0,0,0,0,0,0}; //PA0 sign_Cn
uint8 ADC2_Sequence[]={1,0,0,0,0,0}; //PA1 Ampl1


// CASO 2: lê canal X e canal Y
/*  uint8 ADC1_Sequence[]={0,0,0,0,0,0}; //PA0 sign_Cn
 *  uint8 ADC2_Sequence[]={8,0,0,0,0,0}; //PB0 sign_Cn+4
 */

// CASO 3: lê canal X e amplitude I2
/*  uint8 ADC1_Sequence[]={0,0,0,0,0,0}; //PA0 sign_Cn
 *  uint8 ADC2_Sequence[]={8,0,0,0,0,0}; //PA4 Ampl2
 */


void mede_ADC(){
  //Realiza a medicao das amplitudes vistas nos ADCs e calcula sinais medios;
  //retorna o calculo de amplitude e fase
  digitalWrite(LED, LOW); // Verificação de funcionamento
  // medindo valores:
  start_convertion_dual_channel(adcbuf, NUM_SAMPLES);
  wait_convertion_dual_channel();


uint16_t datav1[NUM_SAMPLES];
uint16_t datav2[NUM_SAMPLES];
    
  // separando valores lidos nos 2 ADCs:
  for(int i=0;i<(NUM_SAMPLES);i++) {
    //datav1[i] = ((adcbuf[i] & 0xFFFF0000) >>16);
    datav1[i] = (adcbuf[i] & 0xFFFF);
    datav2[i] = ((adcbuf[i] & 0xFFFF0000) >>16);
  }

  // calculando amplitudes e fases
  float media1 = sinal_medio (datav1, NUM_SAMPLES);
  calc_dft_singfreq(datav1, freq_sinal, sample_freq, media1, amplit1, phase1, 1000, NUM_SAMPLES);

  float media2 = sinal_medio (datav2, NUM_SAMPLES);
  calc_dft_singfreq(datav2, freq_sinal, sample_freq, media2, amplit2, phase2, 1000, NUM_SAMPLES);

  mediu = true;
  digitalWrite(LED, HIGH); // Verificação de funcionamento
}

void processacomando(){
  //Define a frequencia do sinal lido e o n de amostras - em funcao do comando recebido do master

  comando = Serial.read();
  
  switch (comando) {

    
    case 'i': // inicializa as medidas dos eletrodos
      mede_ADC();
      break;

case '1': // 200Khz 6 pontos (6 pts = 2 ciclos)
      freq_sinal = 200000;
      npontos_base = 3;
      n_pontos_mult = 2;
      tempo_demodulacao = 2;
      NUM_SAMPLES = npontos_base*n_pontos_mult;
      Serial.print("200Khz \t");
      Serial.print("num samples = ");
      Serial.print(NUM_SAMPLES);
      Serial.print("\t tempo de demod = ");
      Serial.println(tempo_demodulacao);
      break;
   
    case '2': // 125Khz 24 pontos (24pts = 5 ciclos)
      freq_sinal = 125000;
      npontos_base = 24;
      n_pontos_mult = 1;
      tempo_demodulacao = 10;
      NUM_SAMPLES = npontos_base*n_pontos_mult;
      Serial.print("125Khz \t");
      Serial.print("num samples = ");
      Serial.print(NUM_SAMPLES);
      Serial.print("\t tempo de demod = ");
      Serial.println(tempo_demodulacao);
      break;
   
    case '3': // 100Khz 12 pontos (12 pts = 2 ciclos)
      freq_sinal = 100000;
      npontos_base = 6;
      n_pontos_mult = 2;
      tempo_demodulacao = 5;
      NUM_SAMPLES = npontos_base*n_pontos_mult;
      Serial.print("100Khz \t");
      Serial.print("num samples = ");
      Serial.print(NUM_SAMPLES);
      Serial.print("\t tempo de demod = ");
      Serial.println(tempo_demodulacao);
      break;
    
    case '4': // 50Khz 24 pontos (24 pts = 2 ciclos)
      freq_sinal = 50000;
      npontos_base = 12;
      n_pontos_mult = 2;
      tempo_demodulacao = 10;
      NUM_SAMPLES = npontos_base*n_pontos_mult;
      Serial.print("50Khz \t");
      Serial.print("num samples = ");
      Serial.print(NUM_SAMPLES);
      Serial.print("\t tempo de demod = ");
      Serial.println(tempo_demodulacao);
      break; 

    case '5': // 5Khz 120 pontos (240 pts = 2 ciclos)
      freq_sinal = 5000;
      npontos_base = 120;
      n_pontos_mult = 2;
      tempo_demodulacao = 10;
      Serial.print("5Khz 240 pontos (240 pts = 2 ciclos) e tempo de demod = ");
      Serial.println(tempo_demodulacao);
      break;
      
    case '-': // diminui tempo para medida e demodulação
      tempo_demodulacao = tempo_demodulacao - 1;
      Serial.print("Tempo de demodulacao = ");
      Serial.println(tempo_demodulacao);
      break; 
      
    case '+': // aumenta tempo para medida e demodulação
      tempo_demodulacao = tempo_demodulacao + 1;
      Serial.print("Tempo de demodulacao = ");
      Serial.println(tempo_demodulacao);
      break; 
      

      
    case 't': // diminui nro de pontos
      if(n_pontos_mult>1){
        n_pontos_mult = n_pontos_mult-1;
        NUM_SAMPLES = npontos_base*n_pontos_mult;
        tempo_demodulacao = 1+(npontos_base*n_pontos_mult)/4;
      }
      else Serial.print("Nro de pontos minimo atingido. ");
      Serial.print("Npontos = ");
      Serial.print(npontos_base*n_pontos_mult);
      Serial.print("; npontos_base = ");
      Serial.print(npontos_base);
      Serial.print("; n_pontos_mult = ");
      Serial.print(n_pontos_mult);
      Serial.print("; tempo_demodulacao = ");
      Serial.println(tempo_demodulacao);
      break;
      
    case 'y': // aumenta nro de pontosNUM_SAMPLES_MAX
      if(((n_pontos_mult+1)*npontos_base) < NUM_SAMPLES_MAX){
        n_pontos_mult = n_pontos_mult+1;
        NUM_SAMPLES = npontos_base*n_pontos_mult;
        tempo_demodulacao = 1+(npontos_base*n_pontos_mult)/4;
      }
      else Serial.print("Nro de pontos maximo atingido. ");
      Serial.print("Npontos = ");
      Serial.print(npontos_base*n_pontos_mult);
      Serial.print("; npontos_base = ");
      Serial.print(npontos_base);
      Serial.print("; n_pontos_mult = ");
      Serial.print(n_pontos_mult);
      Serial.print("; tempo_demodulacao = ");
      Serial.println(tempo_demodulacao);
      break;



   case 'P':
      // imprimindo valores lidos:
      for(int i=0;i<(NUM_SAMPLES);i++) {
        float volts= ((adcbuf[i] & 0xFFFF) / 4095.0)* referenceVolts;
        float voltss=  (((adcbuf[i] & 0xFFFF0000) >>16) / 4095.0)* referenceVolts;
        
          Serial.print("adc1:");
          Serial.print(volts);
          Serial.print("\tadc2:");
          Serial.print(voltss);
          Serial.print("\tamplitude 1: ");
          Serial.print(amplit1);
          Serial.print("\tfase (2-1): ");
          Serial.println(phase2-phase1);
        }
      Serial.println();
      break;

////////////////////////////////////////////////////////////////

    default:
      break;
  }
  comando = 0;
}





////////////////////////////////////////////////////////////////////////////////////
void setup() {


  pinMode(LED, OUTPUT); // LED para verificação de funcionamento do eletrodo
   //digitalWrite(LED, HIGH); // Verificação de funcionamento
  Serial.begin(9600); // só usar para debugar...
  set_adc_dual_channel(PRE_SCALER, ADC_SMPR, CHANNELS_PER_ADC, ADC1_Sequence, ADC2_Sequence, FAST_INTERLEAVED);  // initial ADC1 and ADC2 settings

   
   
}

////////////////////////////////////////////////////////////////////////////////////
void loop() {

  if(Serial.available()){
    processacomando();
  }
}

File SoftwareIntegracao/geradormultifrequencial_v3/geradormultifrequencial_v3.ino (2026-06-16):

/*
 * COMANDOS QUE PODEM SER ENVIADOS A PARTIR DO CONTROLADOR PARA ESSE PERIFERICO
 * 
 * 
 * COMANDOS DE CONFERENCIA
 * 4048 - Retorna a informação de frequência configurada no primeiro gerador de sinal (frequencias de 1kHz a 20 kHz)
 * 4049 - Retorna a informação de frequência configurada no segundo gerador de sinal (frequências de 10kHz a 200 kHz)
 * 
 * 
 * COMANDOS PARA ALTERACAO DA FREQUENCIA NO GERADOR 1
 * 4065 - Altera a frequência do Gerador 1 para 1kHz, ou seja, freq1 = 1000;
 * 4066 - Altera a frequência do Gerador 1 para 2kHz, ou seja, freq1 = 2000;
 * 4067 - Altera a frequência do Gerador 1 para 3kHz, ou seja, freq1 = 3000;
 * 4068 - Altera a frequência do Gerador 1 para 5kHz, ou seja, freq1 = 5000;
 * 4069 - Altera a frequência do Gerador 1 para 10kHz, ou seja, freq1 = 10000;
 * 4070 - Altera a frequência do Gerador 1 para 20kHz, ou seja, freq1 = 20000;
 *
 * 4090 - Altera a frequência do Gerador 1 para 0kHz, ou seja, freq1 = 0; (para desabilitar o uso desse gerador;
 * 
 * 
 *  * COMANDOS PARA ALTERACAO DA FREQUENCIA NO GERADOR 2
 * 4097 - Altera a frequência do Gerador 2 para 10 kHz, ou seja, freq2 = 10000;
 * 4098 - Altera a frequência do Gerador 2 para 20 kHz, ou seja, freq2 = 20000;
 * 4099 - Altera a frequência do Gerador 2 para 30 kHz, ou seja, freq2 = 30000;
 * 4100 - Altera a frequência do Gerador 2 para 50 kHz, ou seja, freq2 = 50000;
 * 4101 - Altera a frequência do Gerador 2 para 100 kHz, ou seja, freq2 = 100000;
 * 4102 - Altera a frequência do Gerador 2 para 150 kHz, ou seja, freq2 = 150000;
 * 4103 - Altera a frequência do Gerador 2 para 200 kHz, ou seja, freq2 = 200000;
 * 
 * 4122- Altera a frequência do Gerador 2 para 0kHz, ou seja, freq2 = 0; (para desabilitar o uso desse gerador;
 * 
 */




// =============================================================================================================
// --- Mapeamento de Bibliotecas ---
#include <Wire_slave.h>


// =============================================================================================================
// --- Mapeamento de Hardware ---
#define W_CLK_2 PA7  //Pino WCLK  do módulo AD9850 - Gerador 2 (amarelo)
#define FQ_UD_2 PA6  //Pino FQUP  do módulo AD9850 - Gerador 2 (laranja)
#define DATA_2 PA5   //Pino data  do módulo AD9850 - Gerador 2 (preto)
#define RESET_2 PA4  //Pino reset do módulo AD9850 - Gerador 2 (verde)

#define W_CLK_1 PB12  //Pino WCLK  do módulo AD9850 - Gerador 1 (amarelo)
#define FQ_UD_1 PB13  //Pino FQUP  do módulo AD9850 - Gerador 1 (laranja)
#define DATA_1 PB14   //Pino data  do módulo AD9850 - Gerador 1 (preto)
#define RESET_1 PB15  //Pino reset do módulo AD9850 - Gerador 1 (cinza)


// =============================================================================================================
// --- Constantes Auxiliares ---
#define AD9850_CLOCK 125000000  //Frequência do cristal do módulo
#define SLAVE_ADDRESS 0x04
//#define DEBUG 0
byte x = 0;

// =============================================================================================================
// --- Funções Auxiliares ---
#define pulseHigh(pin) \
  { \
    digitalWrite(pin, HIGH); \
    digitalWrite(pin, LOW); \
  }
//Cria uma função que se chama "pulseHigh", primeiro escreve o valor lógico "HIGH" nesse pino e, em seguida, escreve o valor lógico "LOW" nesse pino.


// =============================================================================================================
// --- Protótipo das Funções ---
//==========================================
void receiveEvent(int howMany);
void tfr_byte_1(byte data);              //transfere um byte de forma serial, pelo pino DATA
void tfr_byte_2(byte data);              //transfere um byte de forma serial, pelo pino DATA
void sendFrequency_1(double frequency);  //envia a frequência configurada pelo usuário
void sendFrequency_2(double frequency);  //envia a frequência configurada pelo usuário

int aux = 0;
int control = 2;
double freqaux = 0;
long unsigned int freq_1 = 1000;          //local de definição do valor de frequência do sinal desejado no Gerador 1
long unsigned int freq_2 = 10000;         //local de definição do valor de frequência do sinal desejado no Gerador 2
byte auxfreq1 = 65;
byte auxfreq2 = 97;
bool nerr = 1;
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

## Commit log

2023-07-05 Projetos KIcad e Fritzing TIE
    [Barramento_EITduino.fzz, Barramento_EITduino.kicad_pcb, Barramento_EITduino.kicad_sch, Barramento_EITduino_contour.gm1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]
2023-07-06 atualizacao dos valores de capacitores (eletroliticos) da fonte de tensao
    [Fonte_tensao_LM675_v03.kicad_pcb, Fonte_tensao_LM675_v03.kicad_sch]
2023-07-07 revisar alteracoes fonte tensao v3
    [Fonte_tensao_LM675_v03.kicad_sch]
2023-07-07 revisao de v03 para os componentes utilizados no primeiro prototipo
    [Fonte_tensao_LM675_v04.kicad_pcb, Fonte_tensao_LM675_v04.kicad_sch]
2023-07-07 Fonte de tensao v04 - Para fabricacao do segundo prototipo
    [Fonte_tensao_LM675_v04.kicad_pcb, Fonte_tensao_LM675_v04.kicad_sch]
2023-07-07 Mudancas na fonte de corrente monopolar
    [Fonte_corrente_mono.kicad_sch]
2023-07-07 Atribuicao das barras de pinos
    [Fonte_corrente_mono.kicad_sch]
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2023-07-11 alterações Fonte de corrente
    [Fonte_corrente_mono.kicad_pcb, Fonte_corrente_mono.kicad_sch]
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2023-07-12 Descrição do barramento: esquemático
    [Barramento_EITduino.kicad_pcb]
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2023-07-12 Atualização das informações da página do esquemático
    [Gerador_sinais_AD9833.kicad_sch]
2023-07-13 mudanças circuito de condicionamento
    [condicionamento_BIA_v01.kicad_sch]
2023-07-13 Conexão do arduino nano ao I2c 1
    [Gerador_sinais_AD9833.kicad_pcb, Gerador_sinais_AD9833.kicad_sch]
2023-07-13 mudancas comunicacao SPI
    [Gerador_sinais_AD9833.kicad_sch]
2023-07-14 Atualização Fonte de corrente: Implementação do circuito de condicionamento exclusivo na mesma placa
    [Fonte_corrente_mono.kicad_sch]
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2023-07-14 autosave backup
    [Fonte_corrente_mono.kicad_sch]
2023-07-14 atribuição de footprint para todos os componentes da fonte de corrente monopolar
    [Fonte_corrente_mono.kicad_pcb, Fonte_corrente_mono.kicad_sch]
2023-07-14 Mudanças no circuito de condicionamento da fonte e adição de pinos de verificação
    [Fonte_corrente_mono.kicad_sch]
2023-07-14 alterações PCB
    [Fonte_corrente_mono.kicad_pcb, Fonte_corrente_mono.kicad_sch]
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2023-07-15 alterações PCB: tamanho de pad
    [Fonte_corrente_mono.kicad_pcb, Fonte_corrente_mono.kicad_sch]
2023-07-15 arquivos para fabricação
    [Fonte_corrente_mono-B_Cu.gbr, Fonte_corrente_mono-B_Mask.gbr, Fonte_corrente_mono-B_Paste.gbr, Fonte_corrente_mono-B_Silkscreen.gbr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]
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2023-07-17 Arquivos de produção cnc
    [Fonte_corrente_mono-PTH_LIMPO.drl]
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2023-07-17 modificação: pinos de Vref para escolha da tensao de condicionamento
    [condicionamento_BIA_v01.kicad_sch]
2023-07-19 reposicionamento do circuito
    [condicionamento_BIA_v01.kicad_sch]
2023-07-19 Atribuição dos footprints
    [Gerador_sinais_AD9833.kicad_sch]
2023-07-19 Esquema PCB
    [Gerador_sinais_AD9833.kicad_pcb, Gerador_sinais_AD9833.kicad_sch]
2023-07-19 Arquivos para produção
    [Gerador_sinais_AD9833-B_Cu.gbr, Gerador_sinais_AD9833-B_Mask.gbr, Gerador_sinais_AD9833-B_Paste.gbr, Gerador_sinais_AD9833-B_Silkscreen.gbr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]
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2023-07-19 arquivos de produção - furos
    [Gerador_sinais_AD9833-PTH.drl]
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2023-07-21 Lista de materiais
    [Fonte_tensao_LM675_v03_BOM.csv]
2023-07-21 PCB: atualizacao simbolos chave
    [Fonte_tensao_LM675_v03.kicad_pcb, Fonte_tensao_LM675_v03.kicad_sch]
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2023-07-21 correção valores componentes
    [Fonte_tensao_LM675_v03.kicad_pcb, Fonte_tensao_LM675_v03.kicad_sch]
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2023-07-21 arquivos para fabricar a base
    [Barramento_EITduino-B_Cu.gbr, Barramento_EITduino-B_Mask.gbr, Barramento_EITduino-B_Paste.gbr, Barramento_EITduino-B_Silkscreen.gbr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]
2023-07-21 arquivos producao base
    [Barramento_EITduino-B_Cu.gbr, Barramento_EITduino-B_Mask.gbr, Barramento_EITduino-B_Paste.gbr, Barramento_EITduino-B_Silkscreen.gbr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]
2023-07-26 Arquivos para producao PCB
    [condicionamento_BIA_v01-B_Cu.gbr, condicionamento_BIA_v01-B_Mask.gbr, condicionamento_BIA_v01-B_Paste.gbr, condicionamento_BIA_v01-B_Silkscreen.gbr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]
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2023-07-28 circuito de condicionamento e aquuisição de sinal para BIA
    [condicionamento_BIA_v01-B_Cu.gbr, condicionamento_BIA_v01-B_Mask.gbr, condicionamento_BIA_v01-B_Paste.gbr, condicionamento_BIA_v01-B_Silkscreen.gbr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]
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2023-07-28 Esquemático
    [condicionamento_BIA_v01.kicad_sch]
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2023-07-31 correção polaridade capacitor condicionamento
    [condicionamento_BIA_v01.kicad_pcb, condicionamento_BIA_v01.kicad_sch]
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2023-08-01 Nova versao placa condicionamento e aquisicao
    [condicionamento_BIA_v02-B_Cu.gbr, condicionamento_BIA_v02-B_Mask.gbr, condicionamento_BIA_v02-B_Paste.gbr, condicionamento_BIA_v02-B_Silkscreen.gbr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]
2023-08-01 Arquivos fabricação PCB
    [Barramento_EITduino_etiquetas.kicad_pcb, condicionamento_BIA_v02-NPTH-drl_map.gbr, condicionamento_BIA_v02-PTH-drl_map.gbr, condicionamento_BIA_v02-PTH.drl]
2023-08-03 Novos tamanhos de pad do barramento
    [condicionamento_BIA_v02.kicad_pcb]
2023-08-04 arquivos gerber para producao
    [condicionamento_BIA_v02-B_Cu.gbr, condicionamento_BIA_v02-B_Mask.gbr, condicionamento_BIA_v02-B_Paste.gbr, condicionamento_BIA_v02-B_Silkscreen.gbr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]
2023-08-04 arquivos cnc para producao
    [condicionamento_BIA_v02-B_Cu.gbr, condicionamento_BIA_v02-B_Mask.gbr, condicionamento_BIA_v02-B_Paste.gbr, condicionamento_BIA_v02-B_Silkscreen.gbr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]
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2023-08-04 teste cnc
    [teste-CNC-B_Cu.gbr, teste-CNC-B_Mask.gbr, teste-CNC-B_Paste.gbr, teste-CNC-B_Silkscreen.gbr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]
2023-08-07 Novos tamanhos pads
    [condicionamento_BIA_v02-B_Cu.gbr, condicionamento_BIA_v02-B_Mask.gbr, condicionamento_BIA_v02-B_Paste.gbr, condicionamento_BIA_v02-B_Silkscreen.gbr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]
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2023-08-14 Versao 4.1 da fonte de tensão - novos pinos de terra
    [Fonte_tensao_LM675_v04.1.kicad_pcb, Fonte_tensao_LM675_v04.1.kicad_sch, Fonte_tensao_LM675_v04.kicad_pcb]
2023-08-14 Versao 2 do barramento de pinos- novos pinos de terra
    [Barramento_EITduino-B_Cu.gbr, Barramento_EITduino-B_Mask.gbr, Barramento_EITduino-B_Paste.gbr, Barramento_EITduino-B_Silkscreen.gbr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]
2023-08-14 Versao 2 do barramento de pinos - novos pinos de terra
    [Barramento_EITduino_V02.kicad_pcb, Barramento_EITduino_V02.kicad_sch]
2023-08-14 Primeira versao de barramento - apenas um pino de terra
    [Barramento_EITduino.kicad_pcb, Barramento_EITduino.kicad_sch]
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2023-08-22 correcao numeracao
    [Fonte_tensao_LM675_v04.1.kicad_sch]
2023-08-22 numeracao componentes
    [Fonte_tensao_LM675_v04.1.kicad_pcb]
2023-08-22 Adicionando barramento v03
    [Barramento_EITduino_V03.kicad_pcb, Barramento_EITduino_V03.kicad_sch]
2023-08-22 novo barramento v03
    [Barramento_EITduino_V03.kicad_pcb, Barramento_EITduino_V03.kicad_sch]
2023-08-22 fonte tensao v05
    [Fonte_tensao_LM675_v05.kicad_pcb, Fonte_tensao_LM675_v05.kicad_sch]
2023-08-22 Adicionando PCB v05a roteada.
    [Fonte_tensao_LM675_v05a.kicad_pcb, Fonte_tensao_LM675_v05a.kicad_sch]
2023-08-23 Roteamento PCB v05
    [Fonte_tensao_LM675_v05.kicad_pcb]
2023-08-24 placa fonte tensao roteada
    [Fonte_tensao_LM675_v05.kicad_pcb, Fonte_tensao_LM675_v05_planoterra.kicad_pcb, Fonte_tensao_LM675_v05_planoterra.kicad_sch]
2023-08-25 arquivos gerber para fabricacao jlcpcb
    [Fonte_tensao_LM675_v05-B_Cu.gbl, Fonte_tensao_LM675_v05-B_Mask.gbs, Fonte_tensao_LM675_v05-B_Paste.gbp, Fonte_tensao_LM675_v05-B_Silkscreen.gbo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]
2023-08-25 versao para fabricacao jlcpcb revisao Gustavo
    [Fonte_tensao_LM675_v05.kicad_pcb, Fonte_tensao_LM675_v05.kicad_sch, Fonte_tensao_LM675_v05_planoterra.kicad_pcb, Fonte_tensao_LM675_v05_planoterra.kicad_sch]
2023-09-07 Arquivos Gerber para fabricação de PCB JLCPCB
    [Fonte_tensao_LM675_v05-B_Cu.gbl, Fonte_tensao_LM675_v05-B_Mask.gbs, Fonte_tensao_LM675_v05-B_Paste.gbp, Fonte_tensao_LM675_v05-B_Silkscreen.gbo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]
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2023-10-16 dados voluntarios validacao da fase
    [Equacoes_BIA_testes_medidas.ods, Todas_medidas.ods]
2023-10-31 dados voluntarios 1-4
    [Todas_medidas.ods, voluntarios.ods]
2023-10-31 dados voluntarios 5 e 6
    [voluntarios.ods]
2023-11-01 novos voluntarios
    [voluntarios.ods]
2023-11-01 dados 20 voluntarios
    [voluntarios.ods]
2023-11-01 21 e 22
    [voluntarios.ods]
2023-11-01 voluntarios 26
    [voluntarios.ods]
2023-11-01 voluntario 27
    [voluntarios.ods]
2023-11-08 analise de FFM dos voluntarios
    [dados_bioimpedancia.ods, eqs_ffm.csv, eqs_ffm_transposta.csv, ffm.csv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]
2024-02-05 barramento utilizado na fonte de tensao V05/2023
    [Barramento_v04.kicad_pcb, Barramento_v04.kicad_sch]
2024-02-05 primeira versao do gerador - TG
    [Gerador_sinais_AD9833-B_Cu.gbr, Gerador_sinais_AD9833-B_Mask.gbr, Gerador_sinais_AD9833-B_Paste.gbr, Gerador_sinais_AD9833-B_Silkscreen.gbr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]
2024-02-05 Versao para o barramento V04/2024
    [Gerador_sinais_AD9833.kicad_pcb, Gerador_sinais_AD9833.kicad_sch]
2024-02-05 versao para barramento v04
    [Gerador_sinais_AD9833.kicad_pcb, Gerador_sinais_AD9833.kicad_sch]
2024-02-07 mudanca do barramento para a versao V04
    [Gerador_sinais_AD9833.kicad_sch]
2024-02-07 versao TG
    [Fonte_corrente_mono-B_Cu.gbr, Fonte_corrente_mono-B_Mask.gbr, Fonte_corrente_mono-B_Paste.gbr, Fonte_corrente_mono-B_Silkscreen.gbr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]
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
